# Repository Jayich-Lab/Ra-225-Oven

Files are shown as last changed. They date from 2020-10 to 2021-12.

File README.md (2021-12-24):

# Ra-225 Oven
This project is under active development. We are designing an orthotropic oven to be tested alongside the oven documented below. 

Our oven is designed to provide an atomic flux of radium isotopes 224, 225, and 226 that we can use to load our ion traps. We test the oven with analog elements such as strontium and barium. The oven is 3D printed out of Ti-6Al-4V alloy using Direct Metal Laser Sintering (DMLS).

The oven design allows for independent control of 4 oven tubes. Each oven tube can be filled with a seperate isotope/element. Each tube has its own pin on the flange. All 4 tubes share a common ground. 

Image from iOS (1)

### Dimensions V1 Oven (pictured):
  Assembly Height: 28mm. (Including gold sockets, the assembly rests 32.5mm above the flange pins.)
  
  Assembly Length: 28mm.
  
  Assembly Width: 7mm.
  
  Individual Tube Volume: 3uL.
  
  Tube Outer Diameter: 1.5mm.
  
  Tube Inner Diameter: 0.75mm.
  
  Tube Depth: 7mm.
  
### Dimensions V2 Oven:
  Assembly Height: 37mm. (Including gold sockets, the assembly rests 41.5mm above the flange pins.)
  
  Assembly Length: 31mm.
  
  Assembly Width: 8.5mm.
  
  Individual Tube Volume: 10.75uL.
  
  Tube Outer Diameter: 2.2mm.
  
  Tube Inner Diameter: 1.4mm.
  
  Tube Depth: 7mm.
  
### Operating Temperature:
We can run each oven tube at a maximum of 15 amps (limited by the maximum operating current of the flange). We know that the oven reaches temperatures of at least 1000K when we run at 15A, 69W. 

### Chemistry:

Oven tubes are filled using a Hamilton brand syringe. 2 µL, Model 7102 KH SYR, Knurled Hub NDL, 23 ga, 2.75 in, point style 3, Catalog number: 88500
[purchase here](https://www.hamiltoncompany.com/laboratory-products/syringes/88500)

Anolog tests: Grains of Ca and powdered SrCl2, grains of Ca and 0.1M SrCl2 solution, trace amounts of Ca and SrCl2. 

Radium tests: Ra226 and Zirconium, Ra225 and Zirconium, Ra224 and Zirconium. BaCO3 may also be added as a reducing agent.

Note: Ra226, Ra225, and Ra224 are sourced from the alpha decays of Th230, Th229, and Th228 respectively. 

## Diagrams: 

### Resistive heating diagram:
resistive heating diagram

### Tube side view: 
Untitled drawing-22

### Top down view:
Untitled drawing-23

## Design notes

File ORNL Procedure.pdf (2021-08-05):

ORNL-UCSB Radium Oven Procedure

### 1) UCSB Part 1:

1.1) 2 complete ovens have been assembled under clean conditions on 2 seperate flanges. Each oven assembly consists of 4 oven tubes, 1 oven common, 2 2-56 screws, and 1 oven cap for shipping.

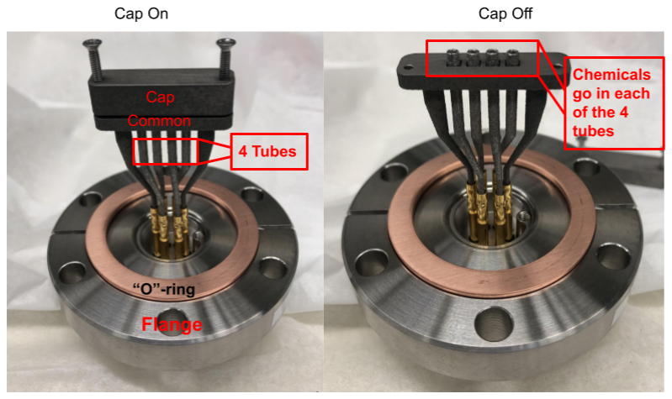
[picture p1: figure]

1.2) The 2 flanges with ovens will be bolted onto opposing sides of a 2.75CF “T” tube, with the third orthogonal end of the “T” tube sealed by a blank. Copper “O”-rings are used to seal each of the ports on the CF “T.”

1.3) Pelican Case 2: The sealed “T” will be loaded into a secure Pelican brand case along with some extra things: a clean plastic bag containing a screwdriver for the 2-56 screws, a wrench for opening the 2.75CF “T,” clean plastic bags for storage, and a clean plastic bag containing extra tubes and 4 clean funnels and screws used for guiding Th and Zr solutions into the oven tubes.

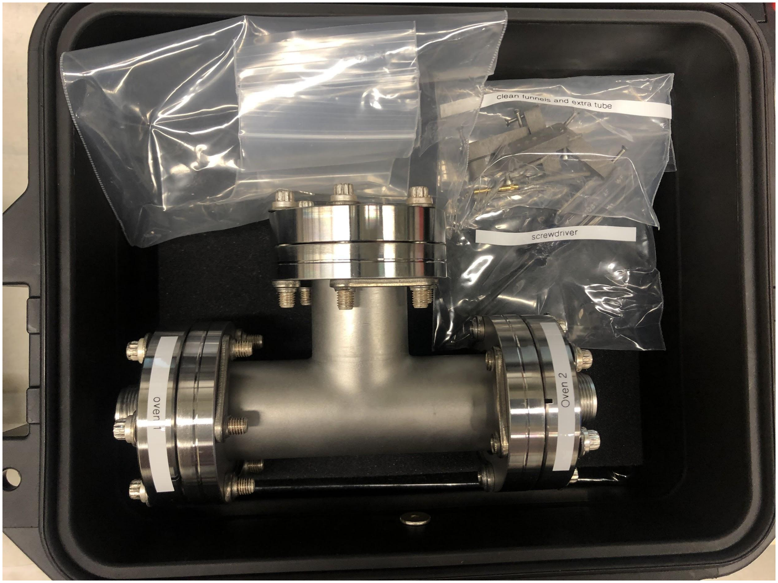
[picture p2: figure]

1.4) Pelican Case 1: An additional Pelican case containing a bottle of Zr powder suspended in water, a bottle of dry BaCO3 powder, a Hamilton brand syringe for loading Zr into the oven tubes, a pair of tweezers for loading BaCO3 powder, and a poking tool for loading BaCO3 powder will be shipped separately.

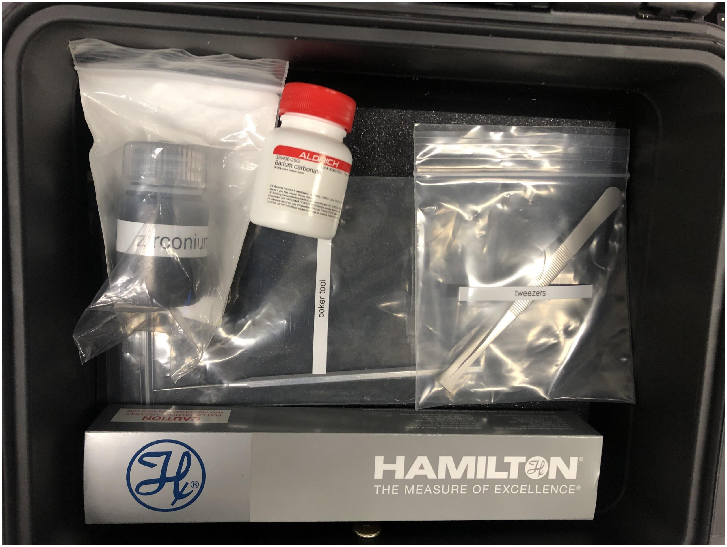
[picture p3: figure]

### 2) Arrival at ORNL:

In a clean area, the cases should be opened and the contents disassembled as specified in the steps below.

2.1) Pelican Case 1:
No disassembly required. Open the case and check to see that the chemical bottles, the syringe, the poker tool, and the tweezers arrived safely.
2.2) Pelican Case 2:
Open the case. Wearing gloves, unbolt the ends of the 2.75CF “T” labeled “Oven 1” and “Oven 2” using the included socket wrench, (as shown in the picture below). The blank, (the end that has no label), should remain bolted.

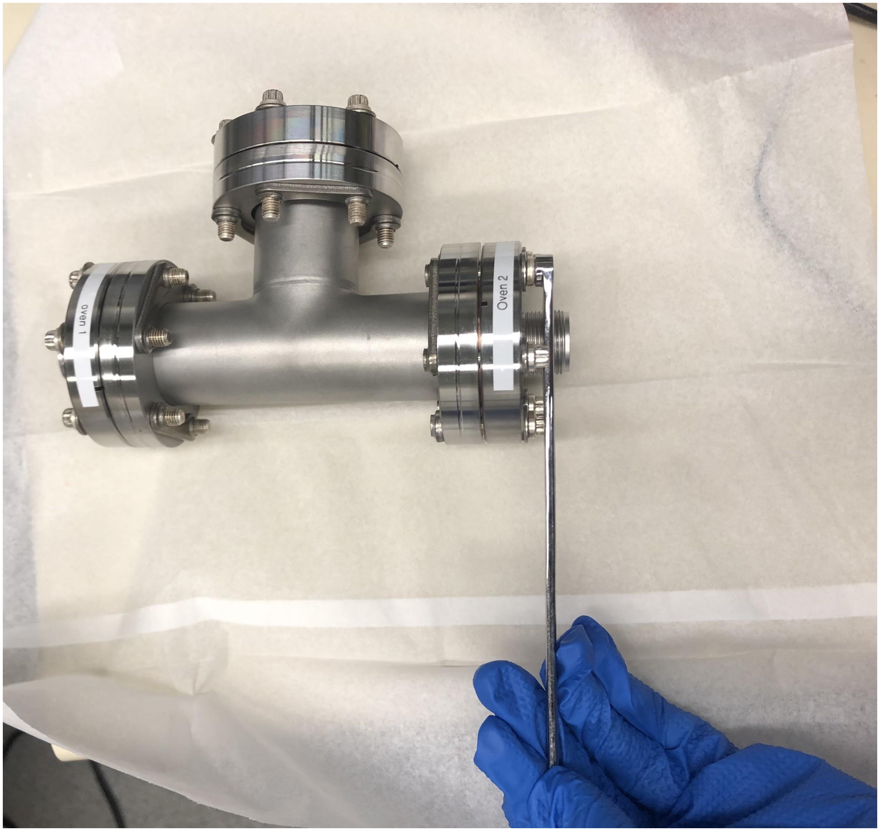
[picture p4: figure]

2.3) After unbolting, place the copper “O”-rings in the clean plastic bag labeled “O-Rings.” Place the bolts, washers, and nuts in another bag labeled “UHV parts.” The two flanges should be inspected, making sure that the oven assemblies on each flange are secure. Store the “T” in a clean place.
2.4) Using the included screwdriver, unscrew the 2 small screws from the top of each oven assembly (as shown in the picture below). Remove the shipping caps and store the screws and the caps in the bag labeled “oven caps.”

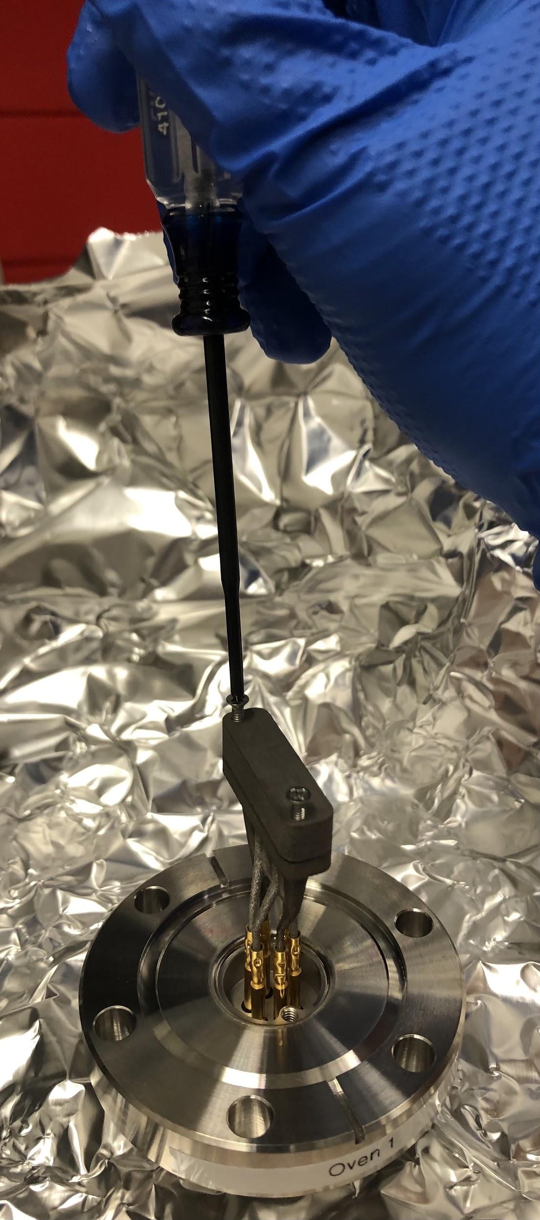
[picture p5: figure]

### 3) Loading the ovens:

Prep:

Due to the fact that our zirconium source is stored as a heterogeneous mixture in water, we need to evaporate and re-mix the mixture in order to know roughly how much Zr we are putting into each tube.

3.1) Shake the Zr bottle. Use a pipette or an ORNL syringe (NOT the Hamilton syringe included in Pelican case 2) to collect a reasonable amount of Zr mixture from the Zr bottle (~1.5mL). Spread the mixture onto a scrapable surface.
3.2) Place the surface with mixture under a heating lamp. Wait until the water has completely evaporated and you are left with only dried Zr powder. This should take ~1/2 hour. Scrape the dried Zr powder off of the surface and into a container.
3.3) Get a low volume vessel where small amounts of chemicals can be mixed. I used a small mortar, but any sloped bottom vessel will work. By weight, measure 0.1g of the freshly dried Zr powder. By volume, measure ~100uL of water (roughly two drops). Mix both quantities in the vessel until the mixture looks like a homogenous silvery liquid with no chunks of Zr. Thorough stirring may be necessary since the Zr powder tends to float on top of the water.

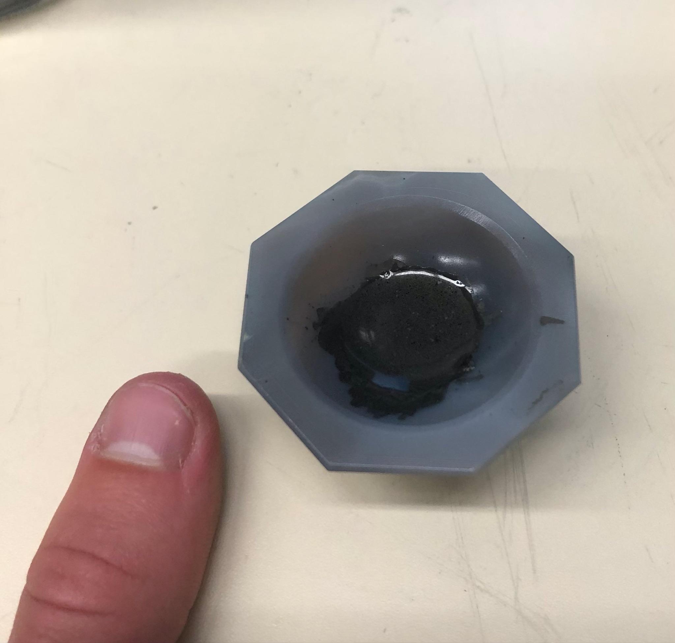
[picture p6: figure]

It is now time to load the ovens:

3.4) Take the oven assembly labeled “oven 1,” and place it into one of the milled aluminum blocks previously shipped from UCSB. The block is used to hold the flange in place.
3.5) Open the plastic bag containing 4 funnels (bag labeled “clean funnels and extra tubes”). Each funnel has a separate label: 224, 225, 226, and Sr. Each funnel already has the necessary screws screwed in.
3.6) Using the included screwdriver, screw the funnel labeled “224” onto the “oven 1” assembly (as shown in the picture below for funnel “225”). The funnel serves as a guide for the syringes and protects the other tubes from contamination. NOTE: It is not critical that the funnels are used for this test with Th-228. However, the funnels must be used for the final experiment, so it will be good practice to use them for this test.

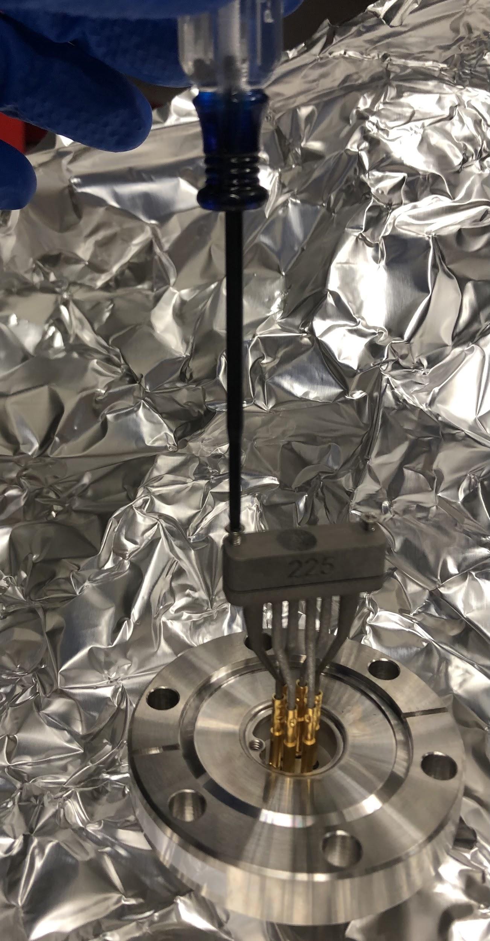
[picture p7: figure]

3.7) Carefully re-mix the Zr mixture from step 3.3 until it is as homogeneous as possible. Fill a 2uL Hamilton syringe (the syringe included in Pelican case 2) with 2uL of the mixture. Insert the syringe through the funnel and down to the bottom of the available tube, and deposit the 2uL of mixture. Repeat this process until the tube is full (~5 times, since the tube has a volume of 10uL).
3.8) After filling the first tube on the first assembly, unscrew the funnel and place it in a clean plastic bag labeled “dirty funnels.”
3.9) Now, take the funnel labeled “225.” Screw the funnel onto the first oven assembly. The funnel will only allow access to the second tube. Repeat step 3.7 until the second tube is full of Zr mixture.
3.10) After filling the second tube on the first assembly, unscrew the 225 funnel from oven assembly 1 and place it into the “dirty funnels” bag.
3.11) Take the funnel labeled “226.” Screw the funnel onto the first oven assembly. Again, the funnel will only allow access to the third. Repeat step 3.7 until the third tube is full of Zr mixture.
3.12) After filling the third tube on the first assembly, unscrew the 226 funnel from the oven assembly and place it into the “dirty funnels” bag.
3.13) Take the funnel labeled “Sr.” Screw the funnel onto the first oven assembly. Again, the funnel will only allow access to the fourth tube. Repeat step 3.7 until the fourth tube is full of Zr mixture..
3.14) After filling the fourth tube on the first assembly, unscrew the Sr funnel from the oven assembly and place it into the “dirty funnels” bag.
3.15) By this step, all 4 tubes on the first oven assembly should be completely full with Zr mixture. Each oven should contain ~10uL of the mixture, corresponding to ~5mg of zirconium.
3.16) Flush the syringe with water. If you do not do this, the Zr will dry inside of the syringe and the syringe will jam. Leave the entire oven assembly, including the flange, out to dry under the heat lamp for ~1 hour. The milled aluminum holders can be used to stabilize the flange while drying. The mixture must completely evaporate before we can proceed.

After Evaporation:

Repeat steps 3.1-3.16. This is necessary because we need to deposit 10mg of Zr in each tube, and 10uL, (the volume of the tube), of Zr mixture corresponds to ~5mg of Zr.

Thorium:

3.17) Take the funnel labeled “224” from the bag. This funnel was already used in steps 3.6 and
3.7. Screw the funnel onto the first oven assembly. Again, the funnel will only allow access to the first tube on the oven assembly.
3.18) Fill a new Hamilton syringe (not used thus far) with 2uL of 1uCi/uL thorium solution. Insert the syringe through the funnel and down to the bottom of the accessible tube, deposit the solution. Repeat until the tube is full.
3.19) After filling the first tube on the first assembly, unscrew the 224 funnel. Take the second oven assembly and place it into one of the milled aluminum blocks previously shipped from UCSB. Screw the 224 funnel onto the second oven assembly. Again, the funnel will only allow access to the first tube on the oven assembly.
3.20) Fill the thorium syringe with 2uL of 1uCi/uL thorium solution. Insert the syringe down to the bottom of the accessible tube, deposit the solution. Repeat until the tube is full.
3.21) After filling the first tube on the second assembly, unscrew the 224 funnel from the oven assembly and dispose of it.
3.22) Take the funnel labeled “225” from the bag. This funnel was already used in steps 3.9 and
3.10. Screw the funnel onto the first oven assembly. Again, the funnel will only allow access to the second tube on the oven assembly.
3.23) Fill the thorium syringe with 2uL of 1uCi/uL thorium solution. Insert the syringe through the funnel and down to the bottom of the accessible tube, deposit the solution. Repeat until the tube is full.
3.24) After filling the second tube on the first assembly, unscrew the 225 funnel. Now screw the 225 funnel onto the second oven assembly. Again, the funnel will only allow access to the second tube on the oven assembly.
3.25) Fill the thorium syringe with 2uL of 1uCi/uL thorium solution. Insert the syringe through the funnel and down to the bottom of the accessible tube, deposit the solution. Repeat until the tube is full.
3.26) After filling the second tube on the second assembly, unscrew the 225 funnel from the oven assembly and dispose of it.
3.27) Take the funnel labeled “226” from the bag. This funnel was already used in steps 3.11 and 3.12. Screw the funnel onto the first oven assembly. Again, the funnel will only allow access to the third tube on the oven assembly.

3.28) Fill the thorium syringe with 2uL of 1uCi/uL thorium solution. Insert the syringe through the funnel and down to the bottom of the accessible tube, deposit the solution. Repeat until the tube is full.
3.29) After filling the third tube on the first assembly, unscrew the 226 funnel. Now screw the 226 funnel onto the second oven assembly. Again, the funnel will only allow access to the third tube on the oven assembly.
3.30) Fill the thorium syringe with 2uL of 1uCi/uL thorium solution. Insert the syringe through the funnel and down to the bottom of the accessible tube, deposit the solution. Repeat until the tube is full.
3.31) After filling the third tube on the second assembly, unscrew the 226 funnel from the oven assembly and dispose of it.
3.32) Take the funnel labeled “Sr” from the bag. This funnel was already used in steps 3.13 and
3.14. Screw the funnel onto the first oven assembly. Again, the funnel will only allow access to the fourth tube on the oven assembly.
3.33) Fill the thorium syringe with 2uL of 1uCi/uL thorium solution .Insert the syringe through the funnel and down to the bottom of the accessible tube, deposit the solution. Repeat until the tube is full.
3.34) After filling the fourth tube on the first assembly, unscrew the Sr funnel. Now screw the Sr funnel onto the second oven assembly. Again, the funnel will only allow access to the fourth tube on the oven assembly.
3.35) Fill the thorium syringe with 2uL of 1uCi/uL thorium solution. Insert the syringe through the funnel and down to the bottom of the accessible tube, deposit the solution. Repeat until the tube is full.
3.36) After filling the fourth tube on the second assembly, unscrew the Sr funnel from the oven assembly and dispose of it.
3.37) All 4 tubes of each oven should now be completely filled with 10uL of 1uCi/uL thorium-228 solution. Leave both oven assemblies out under the heat lamp until the thorium solution is dry.

After Final Evaporation

3.38) The ovens should now be completely dry. Take the oven caps and screws from step 2.4 and screw them back onto the complete assemblies. Place the screwdriver back in the screwdriver bag.

### 4) Shipping back to UCSB:

With all tubes on each oven loaded and shipping caps on, it is time to reassemble the 2.75CF “T.”

4.1) Take the copper “O”-rings, bolts, nuts, and washers from step 2.3. Sandwiching the “O”-ring between the flange and the “T,” carefully bolt the first flange with the included oven assembly onto the “T” using the included wrench. Tighten the bolts in a star formation (do not tighten adjacent bolts one after another). The bolts should be reasonably tight, but no need to go crazy. Repeat this process for the second flange. After the process is complete, the “T” should be in the same state as it was upon arrival.
4.2) Place the “T” (with included flanges and oven assemblies) into Pelican case 2. Place the included tools (wrench, screwdriver, funnels) back into their associated bags and into Pelican case 2.
4.3) Place the Zr bottle, BaCO3 bottle, Syringe, and tweezers back into Pelican case 1.
4.4) Ship back to UCSB. Address:

ATTN: Mingyu Fan and Max Ladabaum
Room No. 3448
California NanoSystems Ins
Elings Hall room 3448
University of California, Santa Barbara Santa Barbara, CA 93106-6105 United States

Thank you!!!

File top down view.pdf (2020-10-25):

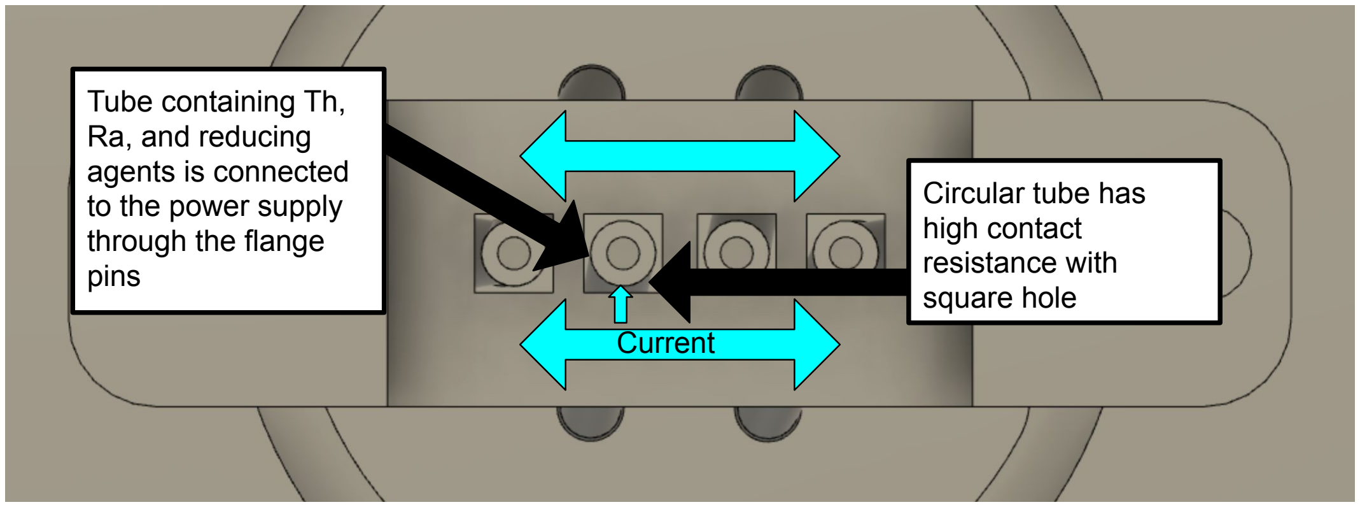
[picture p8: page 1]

Tube containing Th,
Ra, and reducing
agents is connected
to the power supply
through the flange
pins

Current

Circular tube has
high contact
resistance with
square hole

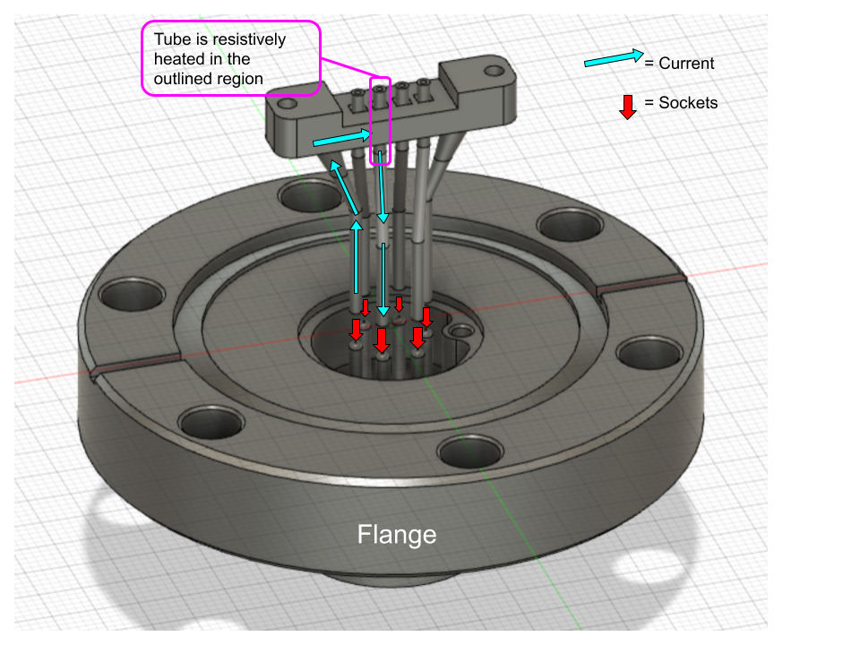
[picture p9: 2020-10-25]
resistive heating diagram.png

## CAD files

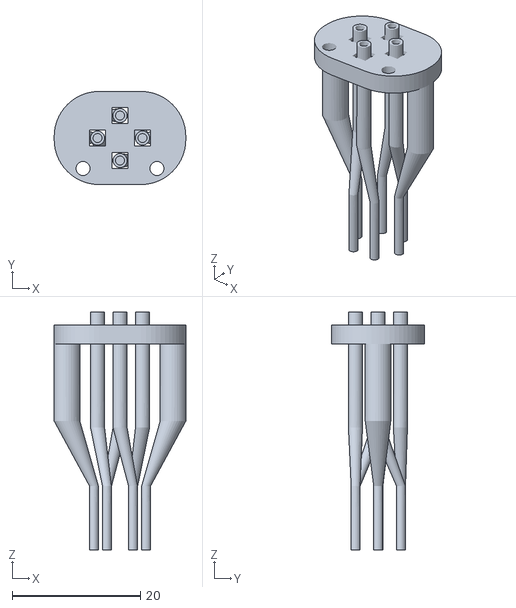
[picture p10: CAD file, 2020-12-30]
wheel trap oven.stl
20.5 x 14.5 x 37.1

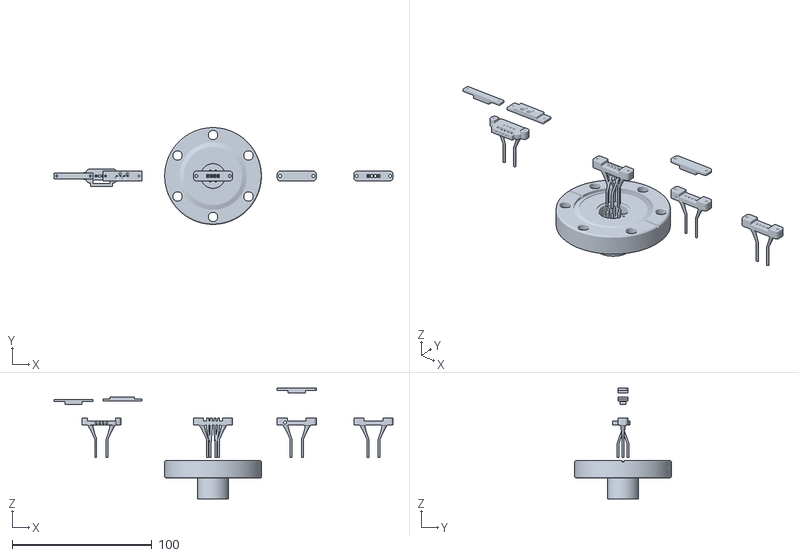
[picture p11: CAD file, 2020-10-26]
ra225oven.stl
243.0 x 69.3 x 79.3

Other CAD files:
raovenV2 v6.ipt

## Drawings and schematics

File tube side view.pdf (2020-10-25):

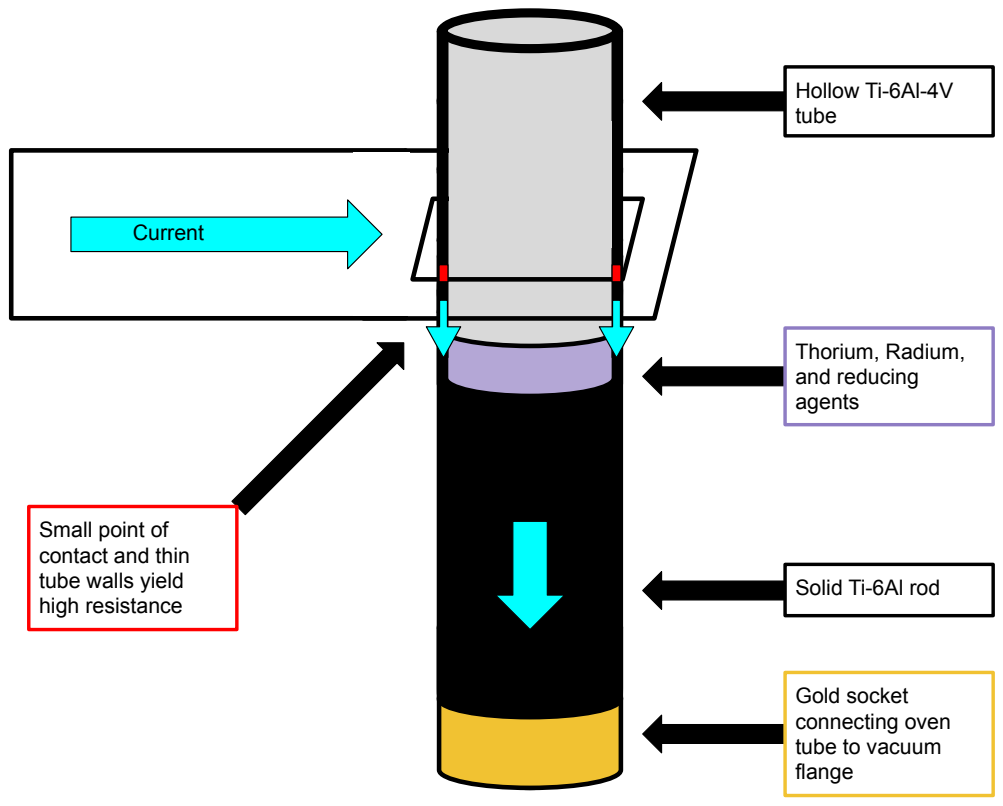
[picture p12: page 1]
Thorium, Radium, and reducing agents; Hollow Ti-6Al-4V tube; Current

Small point of
contact and thin
tube walls yield
high resistance

Solid Ti-6Al rod

Gold socket
connecting oven
tube to vacuum
flange
